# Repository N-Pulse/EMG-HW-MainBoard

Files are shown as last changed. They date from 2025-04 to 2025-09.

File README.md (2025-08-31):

# Electromyography Main Board

This repository contains the PCB design of the EMG bracelet's main board used for EMG signal processing and decoding.
Detailed description of the project can be found in the Documentation folder

This work is licensed under a <a rel="license" href="https://creativecommons.org/licenses/by/4.0/">Creative Commons Attribution 4.0 International License</a>.

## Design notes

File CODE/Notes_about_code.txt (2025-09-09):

NB idk why a .py got inserted in the name, it's really not python

ELEA_Blink : simple blink for ELEA board. All GPIO, UART, SPI etc are already configured (hopefully correctly) in the .ioc file. IMPORTANT : the pre-generated line  PeriphCommonClock_Config() of main.c was commented out because it produced an error that I didn't have time to understand and fix. I think the peripheral clock only concerns some radio stuff, so it should not affect other functions, but who knows ?

ELEA_UART : simple UART communication between STM32 and PC on UART2 using interrupts and callbacks (baud rate 115200). Asks for a key (R,G,B), echoes it back and completes it (R + "ed"). On the Nucleo board this was coded to activate some LEDs, but annoying to set up the pins for that on ELEA. Same remark about PeriphCommonClock_Config() as above.

ELEA_Basic_SPI : it's literally just sending the message "11110001" to the ADC over SPI3. It doesn't mean anything, I just wanted an easily recognizable signal to check on the oscilloscope. Same remark about PeriphCommonClock_Config() as above.

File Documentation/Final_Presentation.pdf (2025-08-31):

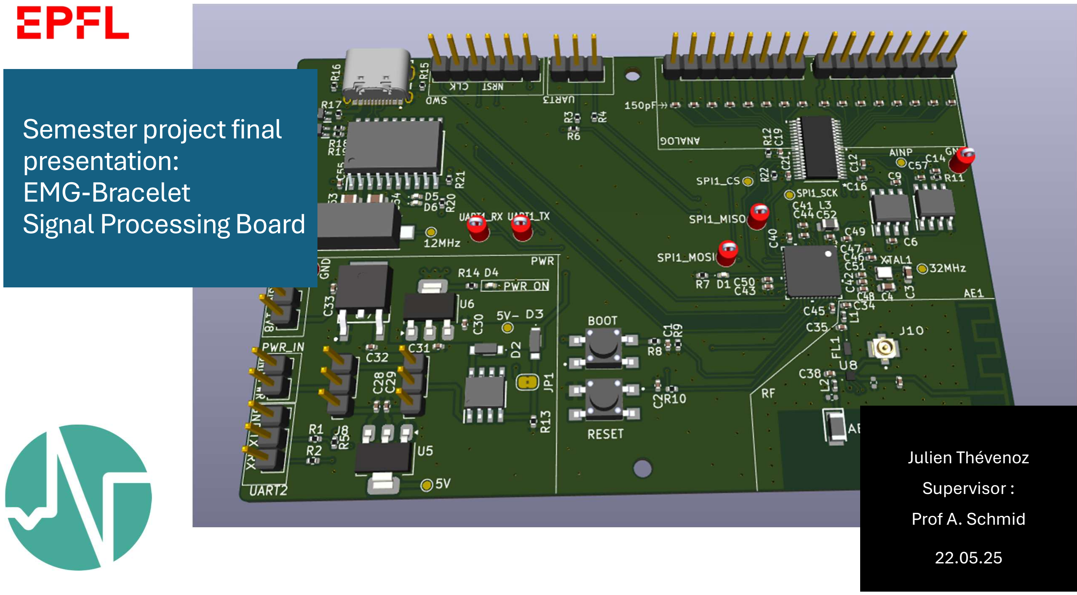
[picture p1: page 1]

## Semester project final presentation: EMG-Bracelet Signal Processing Board

Julien Thévenoz
Supervisor :
Prof A. Schmid

22.05.25

## Table of contents

### 1) Project motivation & goals

### 2) Requirements

### 3) Design choice : Board as prototype

### 4) Product version 1 4.1) Block Diagram 4.2) Schematic 4.3) PCB layout

### 5) Challenges

### 6) Progress

### 7) Demonstrations

### 8) References

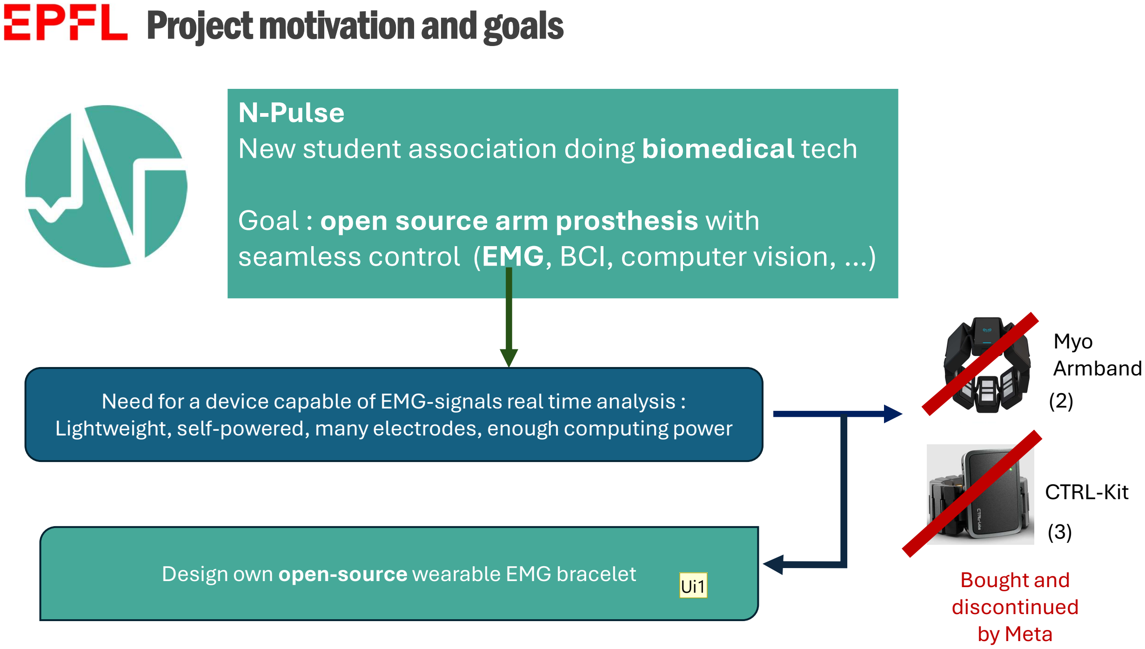
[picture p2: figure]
Project motivation and goals; N-Pulse; Goal : open source arm prosthesis with; CTRL-Kit; Bought and discontinued by Meta; Myo Armband

## New student association doing biomedical tech

## seamless control (EMG, BCI, computer vision, …)

Need for a device capable of EMG-signals real time analysis : Lightweight, self-powered, many electrodes, enough computing power

Design own open-source wearable EMG bracelet

Slide 3

Ui1 | "EMG analysis" implies it only does signal processing, but in our case it also does signal acquisition.=> I would simply say "EMG bracelet". Utilisateur invité, 2025-05-21T22:29:21.107

## Project motivation and goals

«Development of an open-source EMG armband for Hand Gesture Estimation” Semester project by R. Danylovych and E. Massonnet at labs INL & TNE

Based on a design by eLiONS lab (Politecnico Torino) [1] [2] First prototype of EMG signal acquisition modules and bracelet architecture BUT no time to develop module to analyze the signals

Autumn
2024

Spring 2025

ML Semester project proposition : «EMG Signal Processing Board»

•Standalone, wearable, light , ajustable bracelet •Hand gesture detection from EMG signals

•Open-source and documented

Develop the hardware to analyze the EMG signals :

- Able to run compact ML algorithm such as [3] on- board and in real time
- Transmit results wirelessly and physically
- Central piece of the EMG bracelet (powers the rest)

The signal processing board is a component of the N-Pulse EMG Bracelet project :

## Requirements

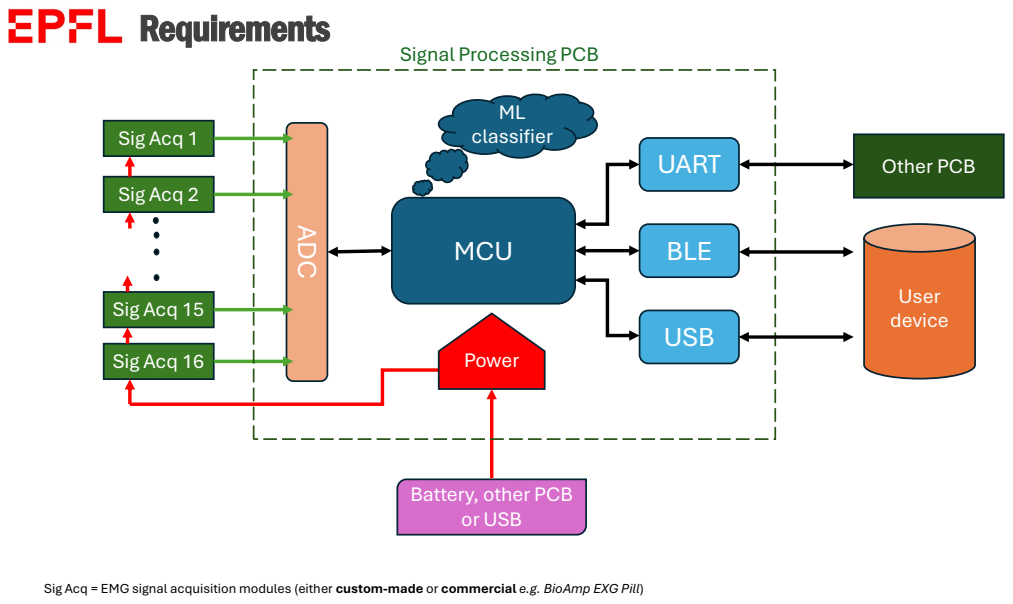
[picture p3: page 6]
MCU ADC; Sig Acq 1; Sig Acq 2; Sig Acq 16; BLE; USB; UART; Sig Acq 15; Power; Other PCB; ML classifier; User device

Signal Processing PCB

Battery, other PCB
or USB

Sig Acq = EMG signal acquisition modules (either custom-made or commercial e.g. BioAmp EXG Pill)

## Requirements

Paper [3] proposes a model with ~7000 parameters to do hand gesture classification This amounts to ~55 kBytes (float double precision 8 Bytes).
Another paper proposes a model with 400’000 parameters [4] ~ 2.6 Mbytes, and then others with even more.
We want to base software on [3] and decided that a flash memory of 2 MB should be enough. For RAM, we calculated that 1s of data ~ 100kBytes.

16 channels @ 800 Hz each --> ADC sampling rate > 12 800 Hz. But accounting for channel switching, non-ideal SigAcq modules etc -> decided 100 Samples per Second strict minimum

Enough FLASH, RAM and clock frequency to run on-board ML algorithm in real-time.
MCU | Bluetooth capability. ADC

## Design choice : board as prototype

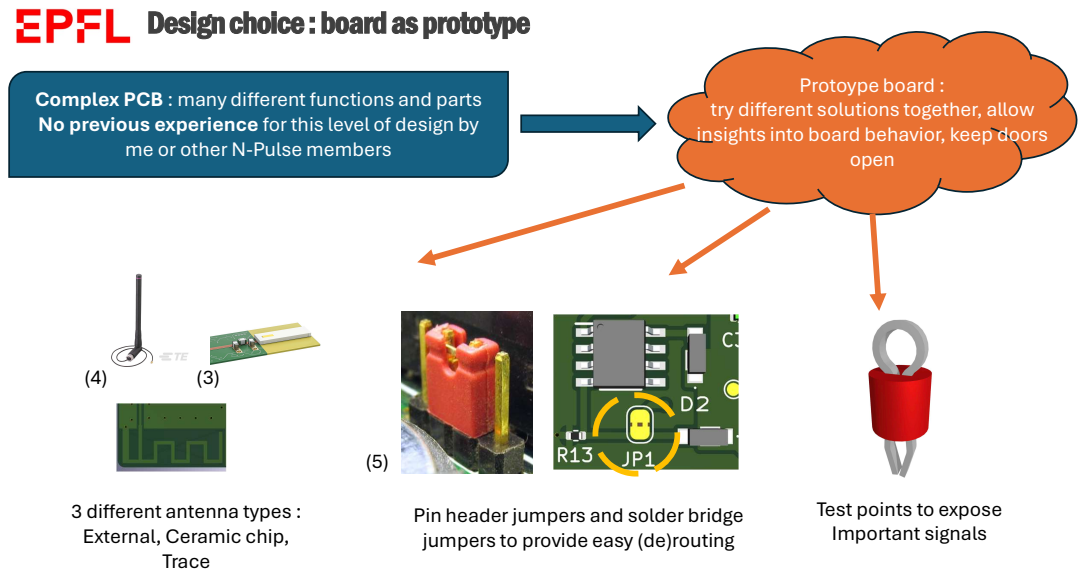
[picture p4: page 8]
Protoype board :; open; Trace

Complex PCB : many different functions and parts
No previous experience for this level of design by

try different solutions together, allow
insights into board behavior, keep doors

me or other N-Pulse members

Test points to expose
Important signals

3 different antenna types :
External, Ceramic chip,

Pin header jumpers and solder bridge
jumpers to provide easy (de)routing

## Signal Processing Board : Version 1

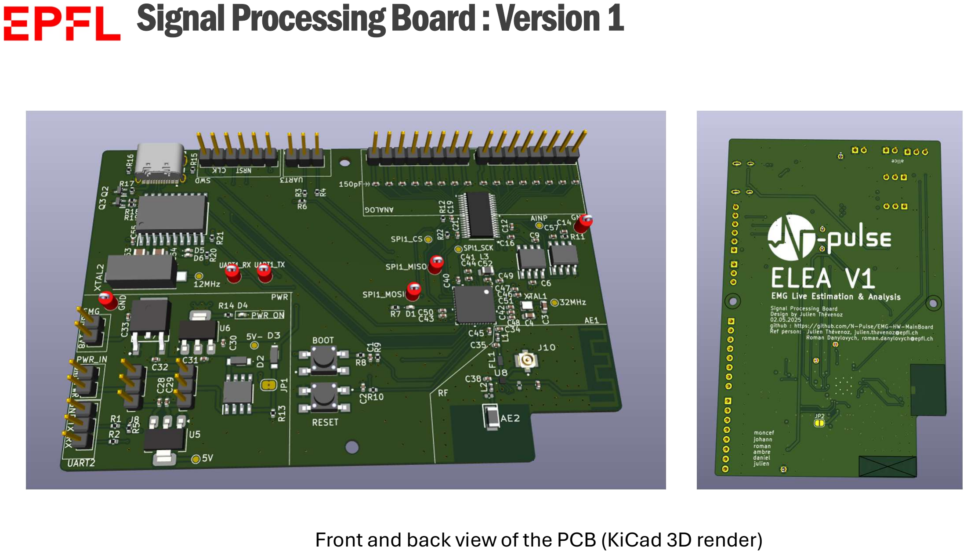
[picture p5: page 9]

Front and back view of the PCB (KiCad 3D render)

## Block diagram

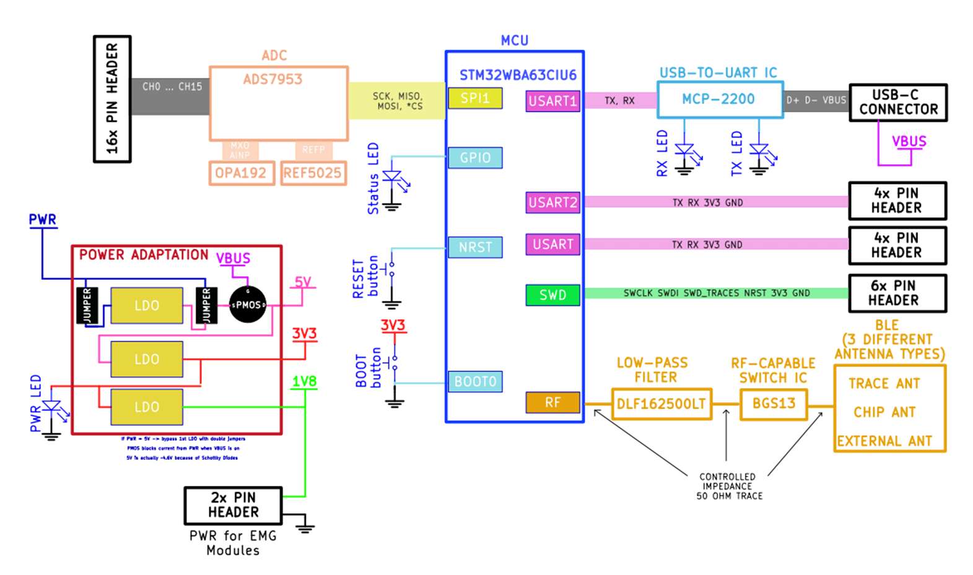
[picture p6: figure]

## Schematic

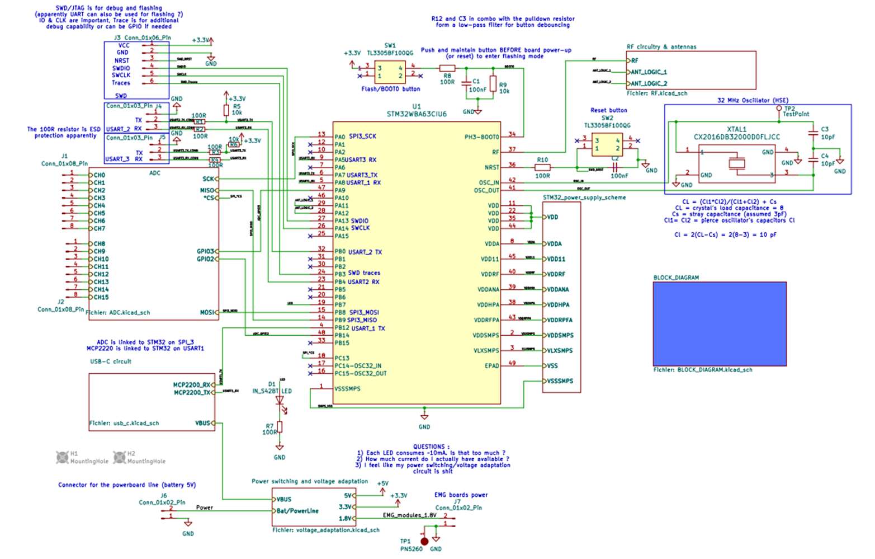
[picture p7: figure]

Electronic schematic main page

## Schematic

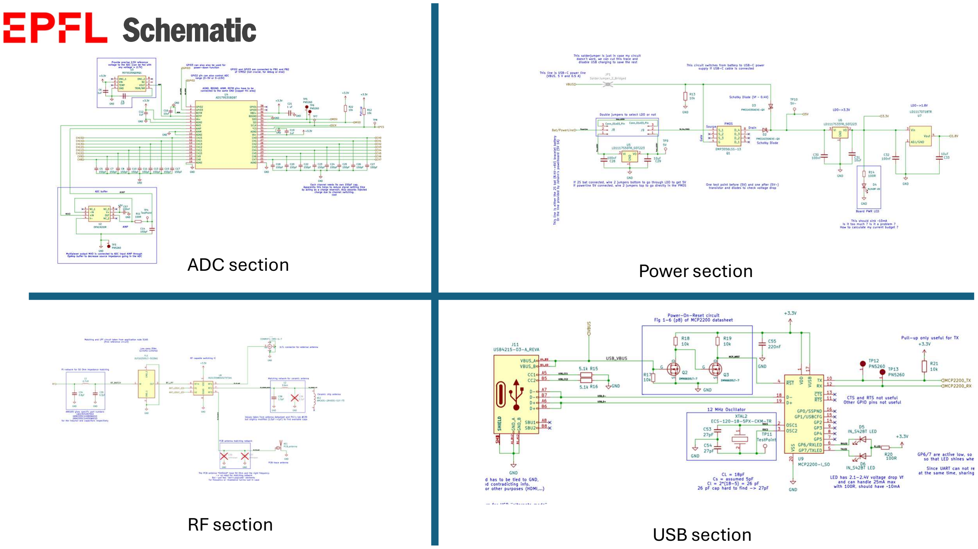
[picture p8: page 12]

RF section

Power section

USB section

ADC section

## PCB LAYOUT – 4 LAYERS

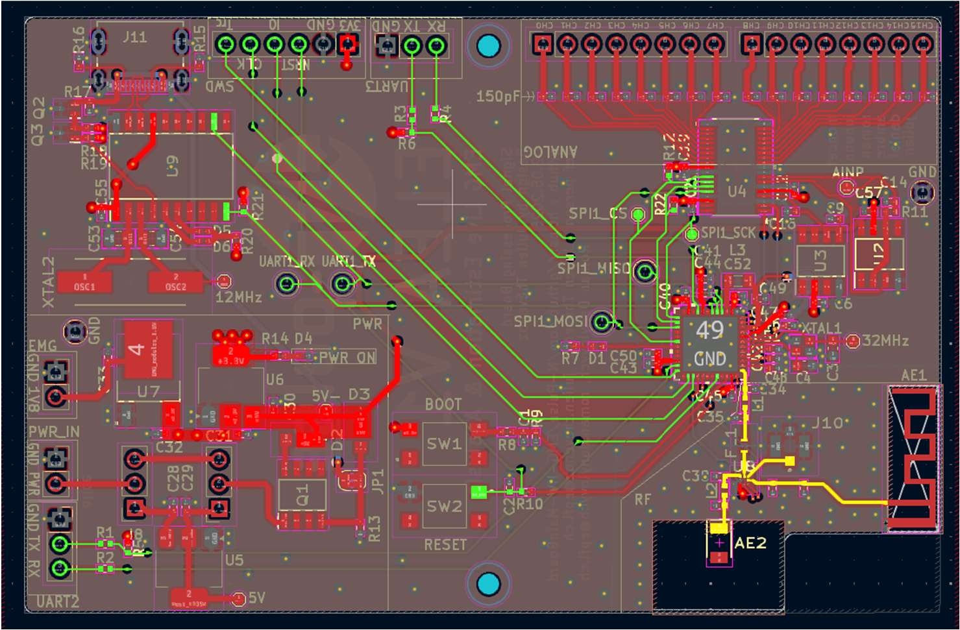
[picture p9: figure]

## PCB LAYOUT

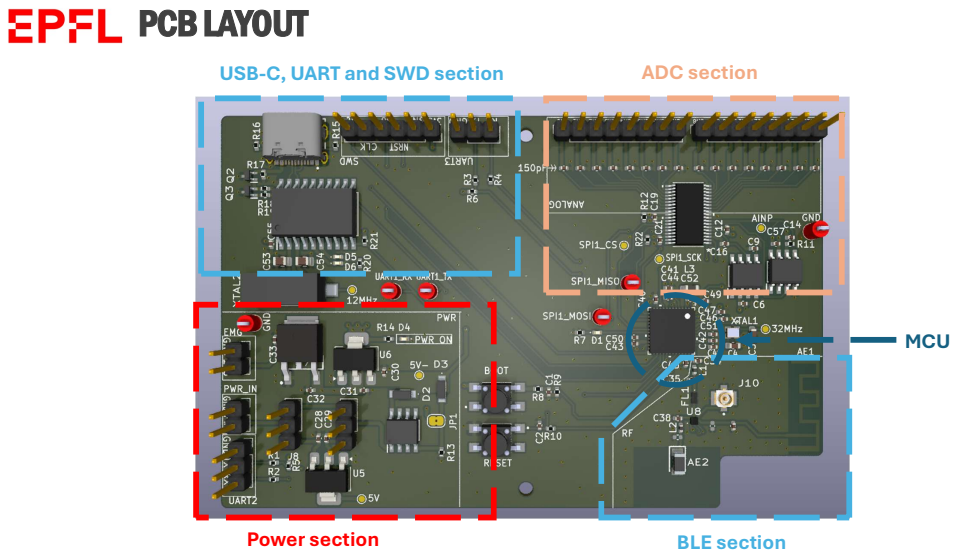
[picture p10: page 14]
Power section; BLE section; USB-C, UART and SWD section; ADC section; MCU

## PCB LAYOUT

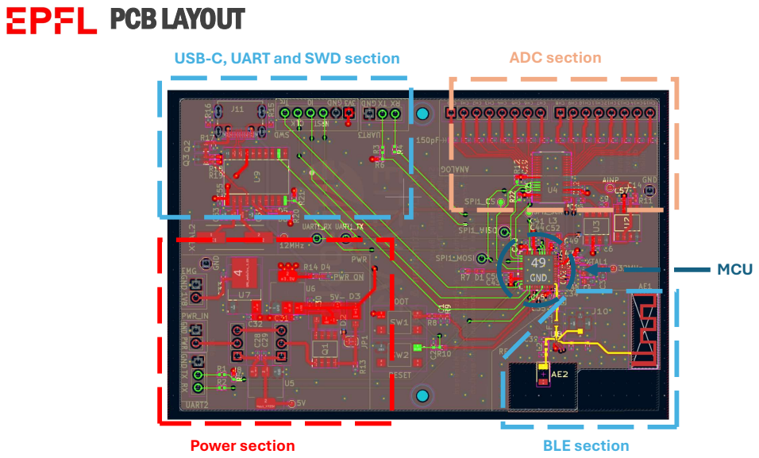
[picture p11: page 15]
Power section; BLE section; USB-C, UART and SWD section; ADC section; MCU

## PCB LAYOUT – 4 LAYERS

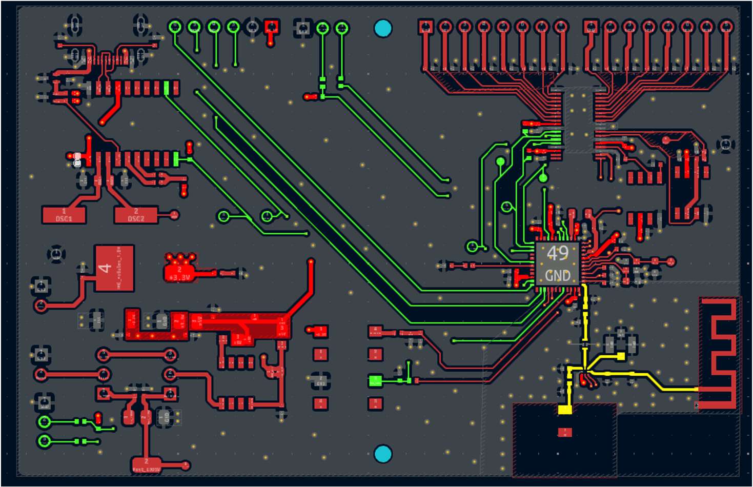
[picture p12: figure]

## PCB LAYOUT – FRONT LAYER (SIGNAL, RF)

## PCB LAYOUT – 2nd LAYER (GND)

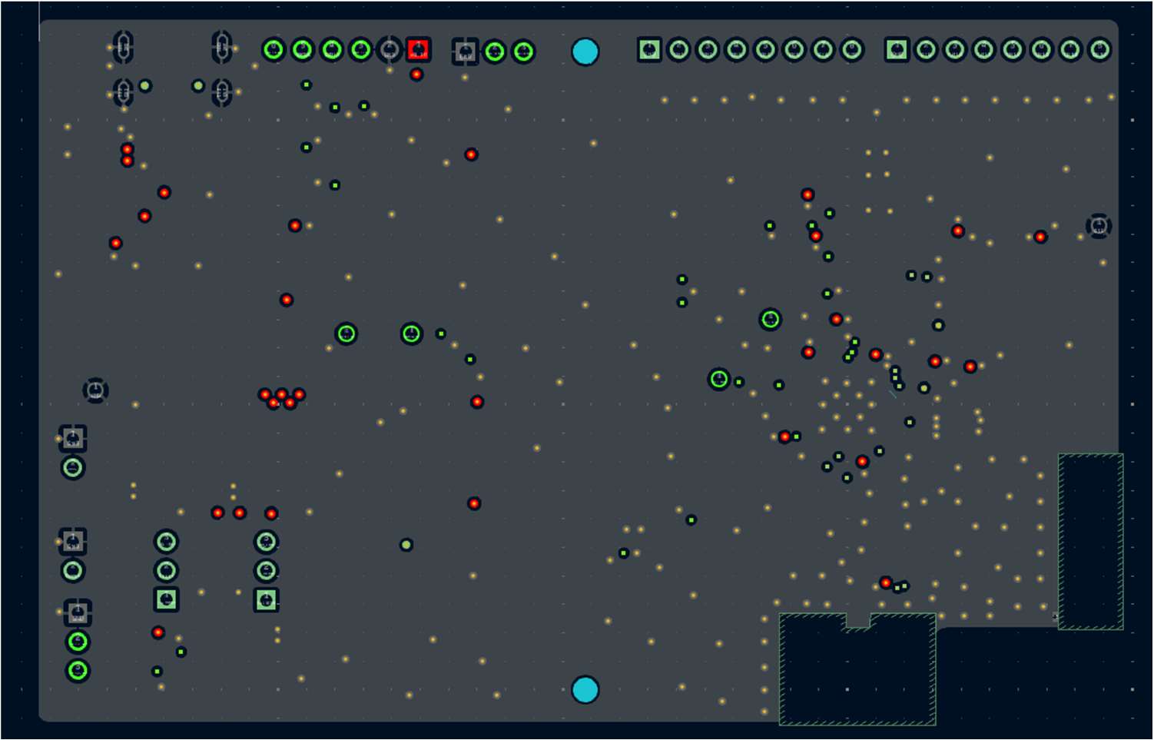
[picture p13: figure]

## PCB LAYOUT – 3rd LAYER (3.3V)

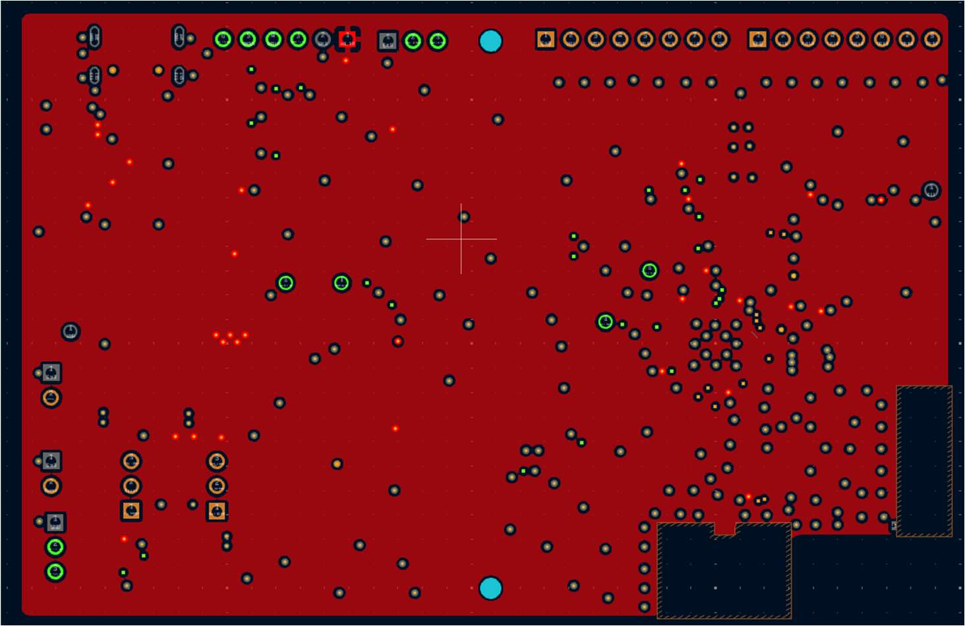
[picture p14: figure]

## PCB LAYOUT – BOTTOM LAYER (SIGNAL)

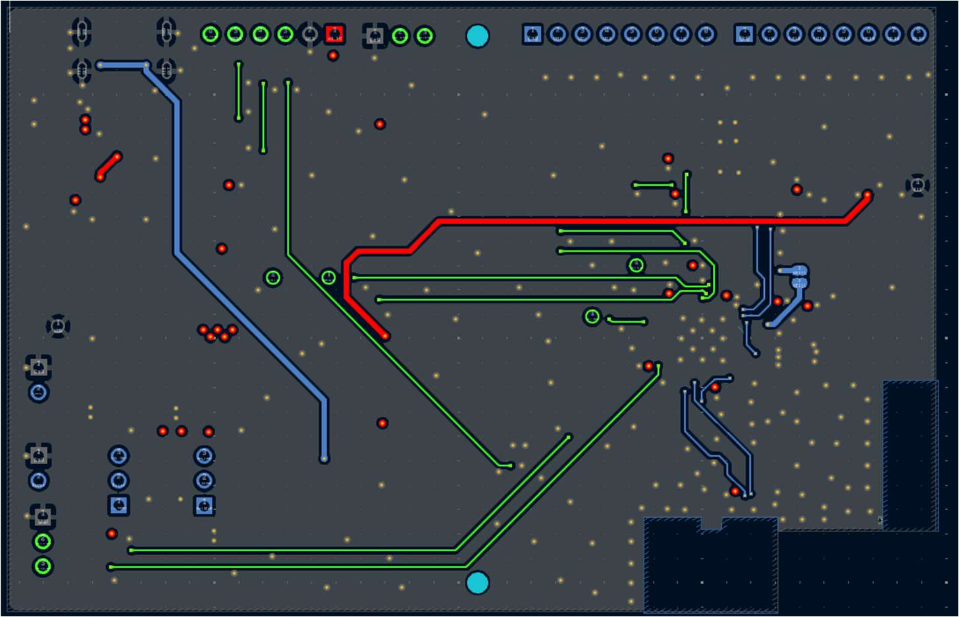
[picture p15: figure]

## Challenges

1) Some goals still slightly vague
2) No prior experience
3) Workload
4) RF

## Self-teaching

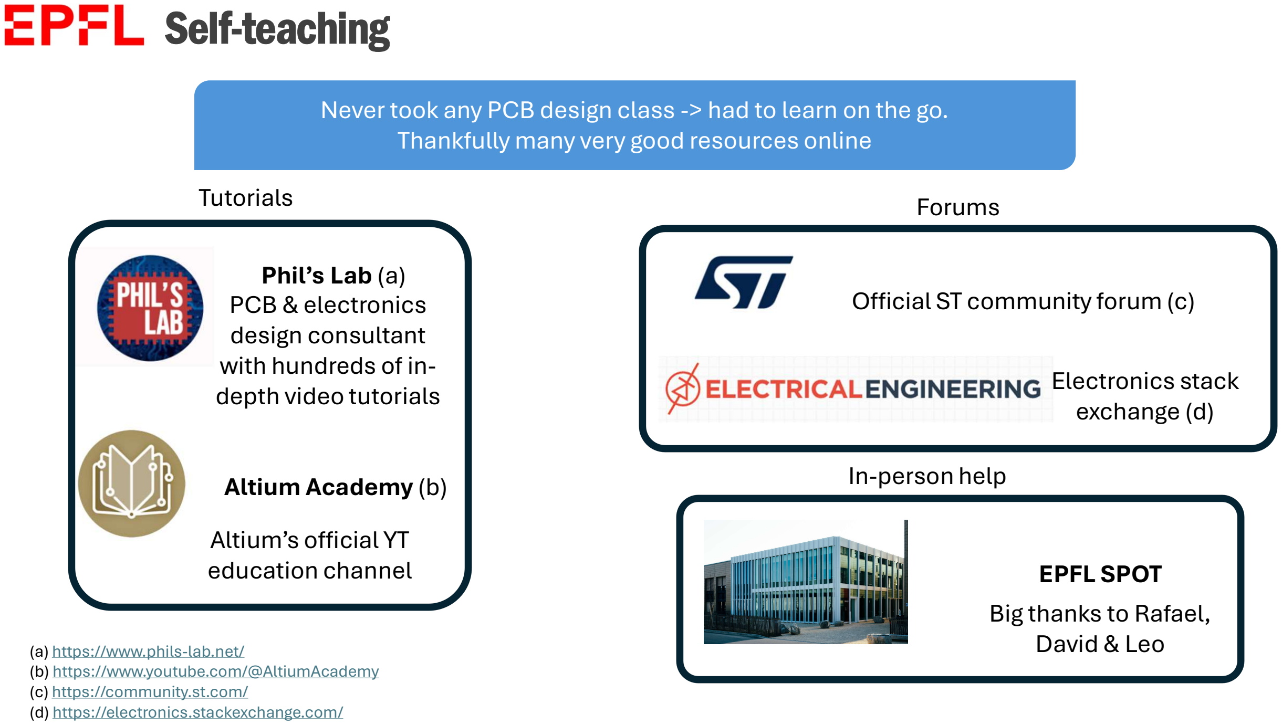
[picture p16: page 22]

(a) https://www.phils-lab.net/
(b) https://www.youtube.com/@AltiumAcademy
(c) https://community.st.com/
(d) https://electronics.stackexchange.com/

Never took any PCB design class -> had to learn on the go. Thankfully many very good resources online

Tutorials

PCB & electronics
design consultant
with hundreds of indepth video tutorials

Altium’s official YT
education channel

Forums

In-person help

Electronics stack
exchange (d)

Phil’s Lab (a)

Altium Academy (b)

EPFL SPOT
Big thanks to Rafael,
David & Leo

Official ST community forum (c)

## Progress so far

- Design
- List of improvement ideas for next iteration
- Extensive list of notes on conception process
- Assemble
- Test individual composants
- Shape improvement ideas and notes into a coherent tutorial N-Pulse members

## Demonstrations : UART communication

Goal : Use UART to command Nucleo Board (STM32) to switch LEDs on/off from PC

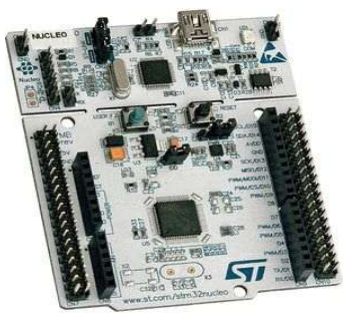
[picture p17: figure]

ST Nucleo F446RE board (6)

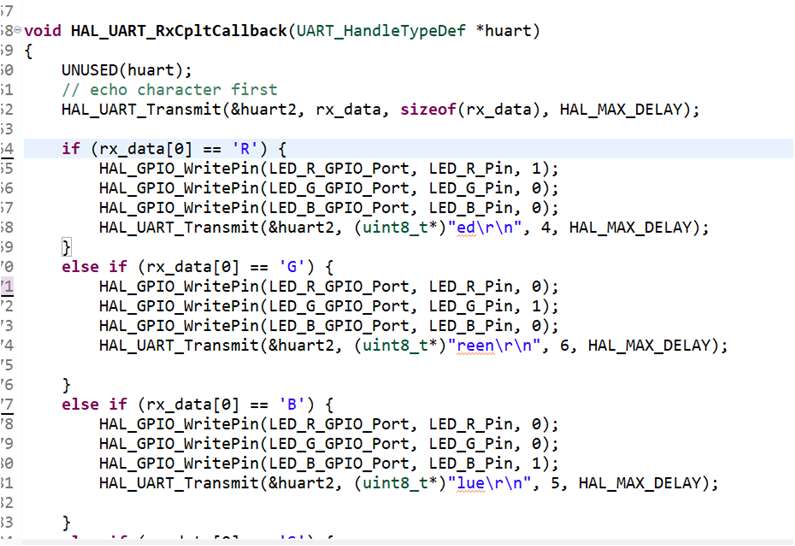
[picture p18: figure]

Code snippet : using interrupt callbacks to command LEDs in non-blocking way
(in STM32CubeIDE)

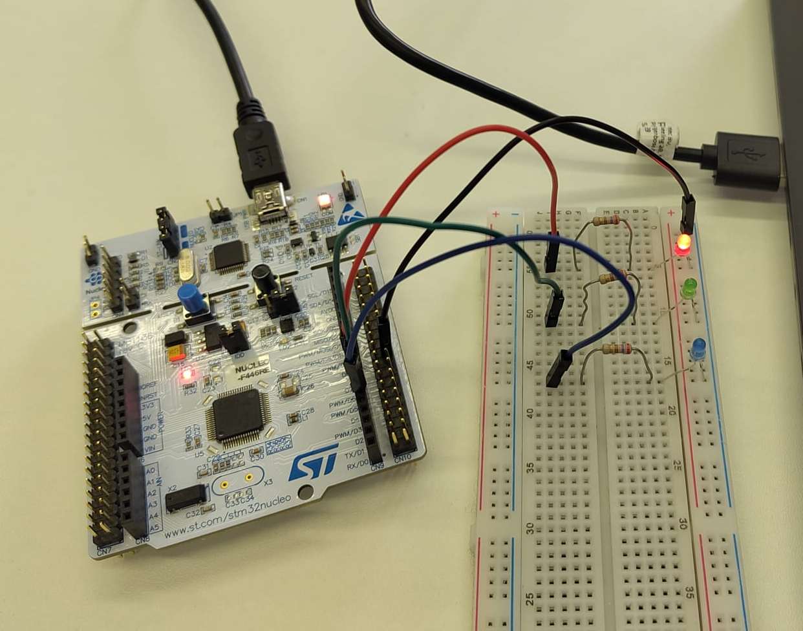
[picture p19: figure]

Setup

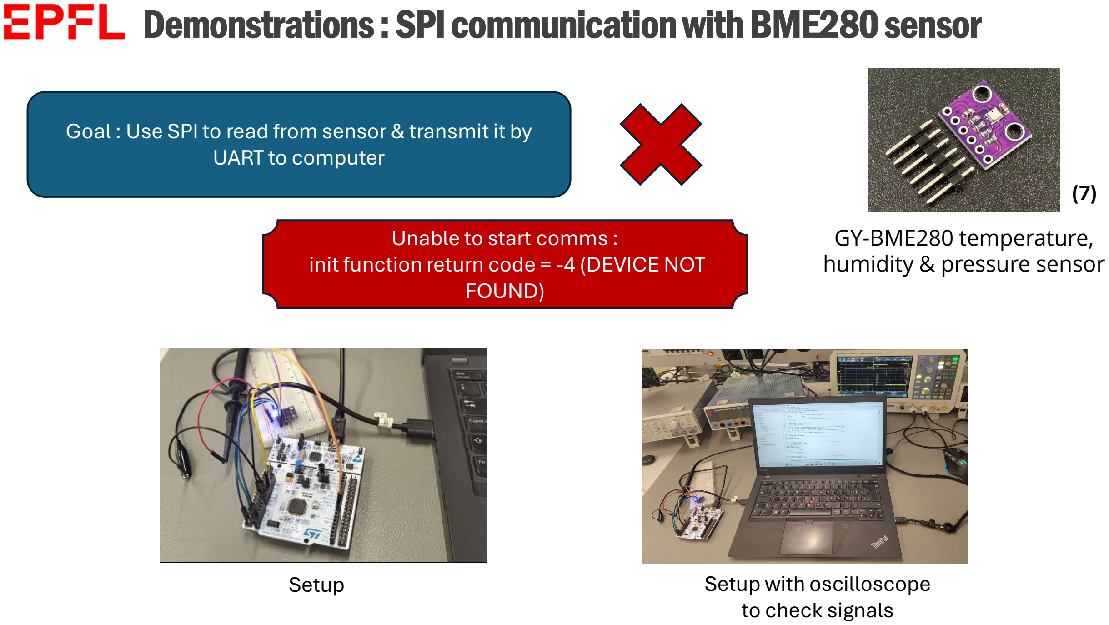
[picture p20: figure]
UART to computer; GY-BME280 temperature, humidity & pressure sensor; Unable to start comms :; FOUND); Setup with oscilloscope to check signals; Setup

## Demonstrations : SPI communication with BME280 sensor

Goal : Use SPI to read from sensor & transmit it by

init function return code = -4 (DEVICE NOT

## Demonstrations : SPI communication with BME280 sensor

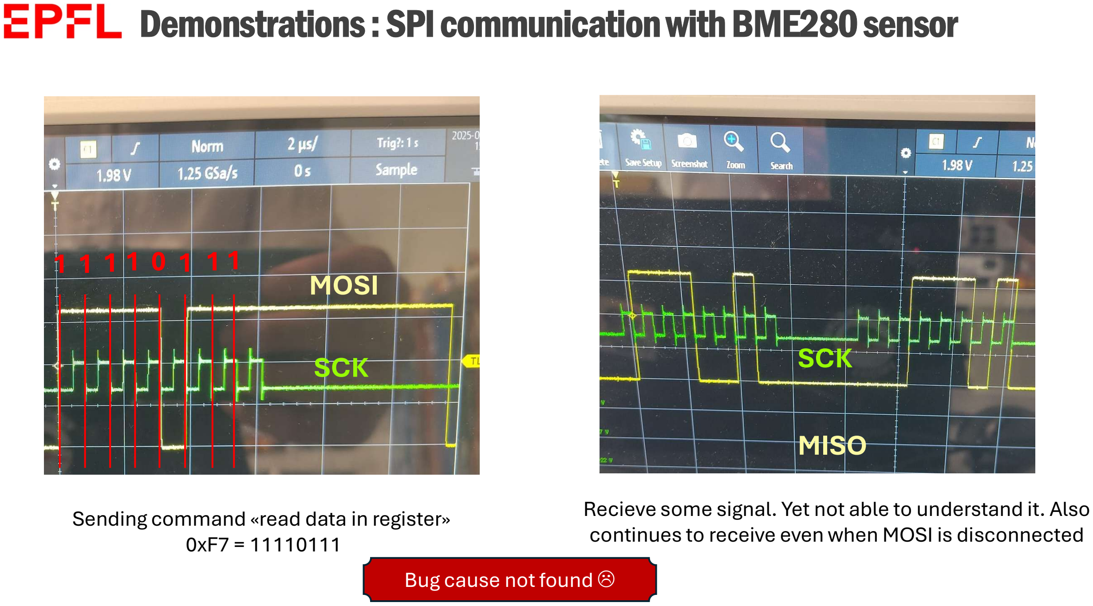
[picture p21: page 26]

1 1 1 1 0 1 1 1

## SCK

## MOSI

Sending command «read data in register» 0xF7 = 11110111

## SCK

## MISO

Recieve some signal. Yet not able to understand it. Also continues to receive even when MOSI is disconnected Bug cause not found

## References

Images
(1) https://wearables.com/products/myo
(2) https://www.curtisbarbre.com/ctrl-kit
(3) https://www.analogictips.com/matching-service-optimizes-gsm-900-wifi-bluetooth-gps-gnss-zigbee-4g-lte-antenna-placement/
(4) https://www.te.com/en/product-L9000097-01.html
(5) https://en.wikipedia.org/wiki/Pin_header#/media/File:Jumper_on_motherboard.jpg
(6) https://media.distrelec.com/Web/WebShopImages/portrait_medium/23/3f/st-nucleo-30009233f.jpg
(7) https://protosupplies.com/product/gy-bme280-pressure-humidity-temperature-sensor-module/
(8) https://cdn.myportfolio.com/645ef5b2f82fdeaf819364ecd9d55d6c/249fac0f-5e46-40cb-a0d7-fa4df5d45ae8_car_4x3.jpg?h=e5b7b4d92b4ce4867a731d0a88e68f27

## References

Papers
[1] A. Mongardi et al., "Hand Gestures Recognition for Human-Machine Interfaces: A Low-Power Bio-Inspired Armband," in IEEE Transactions on Biomedical Circuits and Systems, vol. 16, no. 6, pp. 1348-1365, Dec. 2022, doi: 10.1109/TBCAS.2022.3211424.
[2] F. Rossi, A. Mongardi, P. M. Ros, M. R. Roch, M. Martina and D. Demarchi, "Tutorial: A Versatile Bio-Inspired System for Processing and Transmission of Muhttps://cdn.myportfolio.com/645ef5b2f82fdeaf819364ecd9d55d6c/249fac0f-5e46-40cb-a0d7-fa4df5d45ae8_car_4x3.jpg?h=e5b7b4d92b4ce4867a731d0a88e68f27scular Information," in IEEE Sensors Journal, vol. 21, no. 20, pp. 22285-22303, 15 Oct.15, 2021, doi: 10.1109/JSEN.2021.3103608.
[3] Kalbasi, Mohammad & Shaeri, Mohammad & Mendez, Vincent & Shokur, Solaiman & Micera, Silvestro & Shoaran, Mahsa. (2024). A Hardware-Efficient EMG Decoder with an Attractor-based Neural Network for Next-Generation Hand Prostheses. 10.48550/arXiv.2405.20052.
[4] A. Ameri, M. A. Akhaee, E. Scheme, and K. Englehart, ”Regression convolutional neural network for improved simultaneous EMG control,”
Journal of Neural Engineering, vol. 16, no. 3, 2019, Art. no. 036015.

## Questions

## Thank you for listening

## Questions ?

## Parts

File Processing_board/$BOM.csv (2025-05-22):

Reference | Qty | Value | DNP | Exclude from Board | MANUFACTURER | Manufacturer_Part_Number | Link
AE1 | 1 | PCB_antenna |  | Exclure du PCB
AE2 | 1 | AMCA31-2R450G-S1F-T3 |  |  | ABRACON | AMCA31-2R450G-S1F-T3 | https://www.mouser.ch/ProductDetail/ABRACON/AMCA31-2R450G-S1F-T3?qs=AAveGqk956GLuOddQEK40Q%3D%3D
C1,C2,C28,C30,C32,C40,C41,C42,C43,C45,C46,C47,C51,C57 | 14 | 100nF |  |  | Samsung Electro-Mechanics | CL05B104KP5VPNC | https://eu.mouser.com/ProductDetail/Samsung-Electro-Mechanics/CL05B104KP5VPNC?qs=gqBM4hNBiUXTv%252BkFO9q2pQ%3D%3D
C3,C4 | 2 | 10pF |  |  | KYOCERA AVX | 0603ZC100KAT2A | https://www.mouser.ch/ProductDetail/KYOCERA-AVX/0603ZC100KAT2A?qs=jGANiKWBgcibzoGXAkKY5Q%3D%3D
C5,C7,C8,C10,C11,C13,C14,C15,C17,C18,C20,C22,C23,C24,C25,C26,C27 | 17 | 150pF |  |  | KEMET | C0402C151K5RACTU | https://www.mouser.ch/ProductDetail/KEMET/C0402C151K5RACTU?qs=bH0hdZQCdBIE%252BjkzdJGatg%3D%3D
C6,C9,C12,C19,C44 | 5 | 1uF |  |  | Samsung Electro-Mechanics | CL05A105KP5NNNC | https://www.mouser.ch/ProductDetail/Samsung-Electro-Mechanics/CL05A105KP5NNNC?qs=X6jEic%2FHinBsUeNeR9HD7w%3D%3D
C16,C29,C31,C33,C50,C52 | 6 | 10uF |  |  | Murata Electronics | GRM155R61A106ME11D | https://www.mouser.ch/ProductDetail/Murata-Electronics/GRM155R61A106ME11D?qs=xZ%2FP%252Ba9zWqZMJSi57Q8OyA%3D%3D
C21 | 1 | 1 uF |  |  | Samsung Electro-Mechanics | CL05A105KP5NNNC | https://www.mouser.ch/ProductDetail/Samsung-Electro-Mechanics/CL05A105KP5NNNC?qs=X6jEic%2FHinBsUeNeR9HD7w%3D%3D
C34 | 1 | 0.8pF |  |  | Murata Electronics | GRM1555C1HR80BA01D | https://www.mouser.ch/ProductDetail/Murata-Electronics/GRM1555C1HR80BA01D?qs=e%252BE4OD6MgMezPYPintwvrA%3D%3D
C35 | 1 | 0.3pF |  |  | Murata Electronics | GRM1555C1HR30WA01D | https://www.mouser.ch/ProductDetail/Murata-Electronics/GRM1555C1HR30WA01D?qs=e%252BE4OD6MgMcS%252BbE0ktTutg%3D%3D
C38 | 1 | 1.5pF |  |  | Walsin | 0402N1R5B100CT | https://www.mouser.ch/ProductDetail/Walsin/0402N1R5B100CT?qs=ZrPdAQfJ6DObCBhS8paADQ%3D%3D
C48 | 1 | 470nF |  |  | KEMET | C0402C473K8RACAUTO7411 | https://www.mouser.ch/ProductDetail/KEMET/C0402C473K8RACAUTO7411?qs=sSYV1F9c5cEF%2FA7Et64KMA%3D%3D
C49 | 1 | 4.7uF |  |  | YAGEO | CC0402KRX5R6BB475 | https://www.mouser.ch/ProductDetail/YAGEO/CC0402KRX5R6BB475?qs=tS%2FAHvPQ%2F57yk%252BaeAkyovA%3D%3D
C53,C54 | 2 | 27pF |  |  | KYOCERA AVX | 08055C270KAT2A | https://www.mouser.ch/ProductDetail/KYOCERA-AVX/08055C270KAT2A?qs=ykEKLGTiBcy%2FccVg1dGO5g%3D%3D
C55 | 1 | 220nF |  |  | Murata Electronics | GRT155R71A224KE01D | https://www.mouser.ch/ProductDetail/Murata-Electronics/GRT155R71A224KE01D?qs=qkDYIeTQ%252BEkMujM%252BGJvzUg%3D%3D
D1,D4,D5,D6 | 4 | IN_S42BT LED |  |  | Inolux | IN-S42BT5G | https://www.mouser.ch/ProductDetail/Inolux/IN-S42BT5G?qs=mAH9sUMRCttW6d2tLN392Q%3D%3D
D2,D3 | 2 | PMEG4030AEXE-QX |  |  | Nexperia | PMEG4030AEXE-QX | https://www.mouser.ch/ProductDetail/Nexperia/PMEG4030AEXE-QX?qs=olJun0bQHM9XKv%2FbcqOajw%3D%3D
FL1 | 1 | DLF162500LT-5028A1 |  |  | TDK | DLF162500LT-5028A1 | https://www.mouser.ch/ProductDetail/TDK/DLF162500LT-5028A1?qs=U%2FZX79kHR%2FlwIbAISCs3qA%3D%3D
H1,H2 | 2 | MountingHole |  | Exclure du PCB
J1,J2 | 2 | Conn_01x08_Pin
J3 | 1 | Conn_01x06_Pin
J4,J5,J8,J9 | 4 | Conn_01x03_Pin
J6,J7 | 2 | Conn_01x02_Pin
J10 | 1 | CONMHF1-SMD-G-T |  |  | TE Connectivity / Linx Technologies | CONMHF1-SMD-G-T | https://www.mouser.ch/ProductDetail/TE-Connectivity-Linx-Technologies/CONMHF1-SMD-G-T?qs=7D1LtPJG0i0JqNJVGTgWfg%3D%3D
J11 | 1 | USB4215-03-A_REVA |  |  | CGT | USB4215-03-A | https://www.mouser.ch/ProductDetail/GCT/USB4215-03-A?qs=IKkN%2F947nfBipec8wvDabA%3D%3D
JP1 | 1 | SolderJumper_2_Bridged
JP2 | 1 | SolderJumper_2_Open
L1 | 1 | 2.7nH |  |  | Murata Electronics | LQG15HS2N7S02D | https://www.mouser.ch/ProductDetail/Murata-Electronics/LQG15HS2N7S02D?qs=ctz47l0uL1AKrLI74yO5Qw%3D%3D
L2 | 1 | 3.9nH |  |  | TE Connectivity / Sigma Inductors | 36550402S3N9T | https://www.mouser.ch/ProductDetail/TE-Connectivity-Sigma-Inductors/36550402S3N9T?qs=i8QVZAFTkqQazOkGct7ESA%3D%3D
L3 | 1 | 2.2uH |  |  | Wurth Elektronik | 74479774222 | https://www.mouser.ch/ProductDetail/Wurth-Elektronik/74479774222?qs=%252BUQ4csG8Rsd58%2FKCVoLnRw%3D%3D
Q1 | 1 | DMP3056LSS-13 |  |  | Diodes Incorporated | DMP3056LSS-13 | https://www.mouser.ch/ProductDetail/Diodes-Incorporated/DMP3056LSS-13?qs=oUsD4qhOtFyEnPLZKitYRA%3D%3D
Q2,Q3 | 2 | DMN66D0LT-7 |  |  | Diodes Incorporated | DMN66D0LT-7 | https://www.mouser.ch/ProductDetail/Diodes-Incorporated/DMN66D0LT-7?qs=ptj1V1atRApcnSIo%2FSL0QQ%3D%3D
R1,R2,R3,R4,R7,R8,R10,R11,R14,R20 | 10 | 100R |  |  | KOA Speer | RK73B1ETTPD101J | https://www.mouser.ch/ProductDetail/KOA-Speer/RK73B1ETTPD101J?qs=7ZBenkSduJQ3N2lLjwh2jA%3D%3D
R5,R6,R9,R12,R13,R17,R18,R19,R21,R22 | 10 | 10k |  |  | Wurth Elektronik | 560112110020 | https://www.mouser.ch/ProductDetail/Wurth-Elektronik/560112110020?qs=mELouGlnn3fA8%252B%2F79%2FueqA%3D%3D
R15,R16 | 2 | 5.1k |  |  | YAGEO | AC0402JR-075K1L | https://www.mouser.ch/ProductDetail/YAGEO/AC0402JR-075K1L?qs=ygRr%2Ftkhtev1AbJgasJMAQ%3D%3D
SW1,SW2 | 2 | TL3305BF100QG |  |  | E-Switch | TL3305BF100QG | https://www.mouser.ch/ProductDetail/E-Switch/TL3305BF100QG?qs=IKkN%2F947nfDIPwqPQja%252BvQ%3D%3D
TP1,TP3,TP5,TP6,TP12,TP13 | 6 | PN5260 |  |  | Keystone | 5260 | https://www.mouser.ch/ProductDetail/Keystone-Electronics/5260?qs=W%2FMpXkg%252BdQ5ZyD03UfNp6A%3D%3D
TP2,TP4,TP7,TP8,TP11 | 5 | TestPoint |  | Exclure du PCB
TP9 | 1 | 5V |  | Exclure du PCB
TP10 | 1 | 5V- |  | Exclure du PCB
U1 | 1 | STM32WBA63CIU6 |  |  | STMicroelectronics | STM32WBA63CIU6 | https://www.mouser.ch/ProductDetail/STMicroelectronics/STM32WBA63CIU6?qs=a2MtRaTmNORvrgIwkIejkg%3D%3D
U2 | 1 | OPA192IDR |  |  | TI | OPA192IDR | https://www.mouser.ch/ProductDetail/Texas-Instruments/OPA192IDR?qs=wrT8kFYR77%252BLV20WgpFlnQ%3D%3D
U3 | 1 | REF5025AQDRQ1 |  |  | TI | REF5025AQDRQ1 | https://www.mouser.ch/ProductDetail/Texas-Instruments/REF5025AQDRQ1?qs=jnnG3uwte7w8iuVSV8mElA%3D%3D
U4 | 1 | ADS7953SBDBT |  |  | TI | ADS7953SBDBT | https://www.mouser.ch/ProductDetail/Texas-Instruments/ADS7953SBDBT?qs=Lv5%252BaqTFJEPgQ17SA2TUyg%3D%3D
U5 | 1 | LD1117S50TR_SOT223 |  |  | STMicroelectronics | LD1117S50TR | https://www.mouser.ch/ProductDetail/STMicroelectronics/LD1117S50TR?qs=eQN2Ig5lfEwsh0kTXN%2FkTg%3D%3D
U6 | 1 | LD1117S33TR_SOT223 |  |  | STMicroelectronics | LD1117S33TR | https://www.mouser.ch/ProductDetail/STMicroelectronics/LD1117S33TR?qs=edoyzKMbmhntQZx4BFmoqw%3D%3D
U7 | 1 | LD1117DT18TR |  |  | STMicroelectronics | LD1117DT18TR | https://www.mouser.ch/ProductDetail/STMicroelectronics/LD1117DT18TR?qs=rkyzKKi%2FrgiTGfkwrcFd%252BA%3D%3D
U8 | 1 | BGS13SN8E6327XTSA1 |  |  | Infineon Technologies | BGS13SN8E6327XTSA1 | https://www.mouser.ch/ProductDetail/Infineon-Technologies/BGS13SN8E6327XTSA1?qs=0DP5yvOrqYmFtfP%252BZ8kQgQ%3D%3D
U9 | 1 | MCP2200-I_SO |  |  | Microchip Technology | MCP2200-I/SO | https://www.mouser.ch/ProductDetail/Microchip-Technology/MCP2200-I-SO?qs=kI7nsUnms46fN8L9VZlJCA%3D%3D
XTAL1 | 1 | CX2016DB32000D0FLJCC |  |  | KYOCERA AVX | CX2016DB32000D0FLJCC | https://www.mouser.ch/ProductDetail/KYOCERA-AVX/CX2016DB32000D0FLJCC?qs=k8ubvZJoN9AkB0G5%2Fsjh3g%3D%3D
XTAL2 | 1 | ECS-120-18-5PX-CKM-TR |  |  | ECS | ECS-120-18-5PX-CKM-TR | https://www.mouser.ch/ProductDetail/ECS/ECS-120-18-5PX-CKM-TR?qs=7MVldsJ5UaxGiQ3V9H8iDw%3D%3D
C36,C37 | 2 | Unknown | DNP | Exclure du PCB
C39 | 1 | 1.5pF | DNP | Exclure du PCB

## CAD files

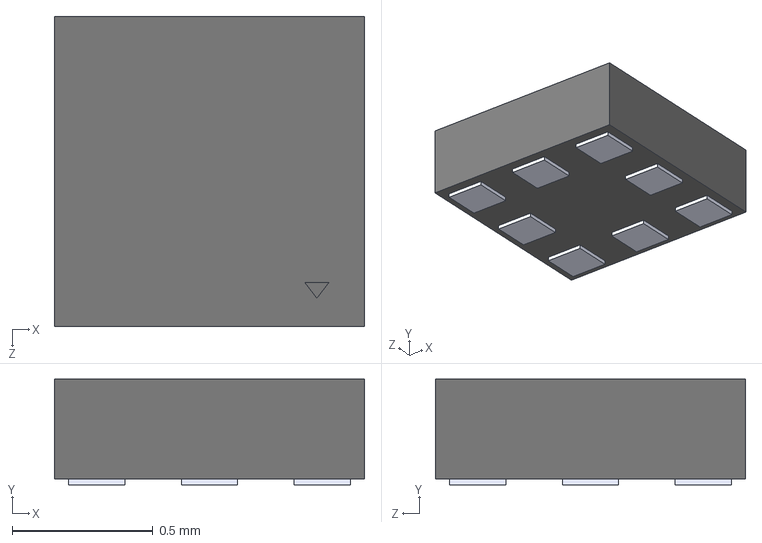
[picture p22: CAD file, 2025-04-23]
Processing_board/CAD models/BGS13SN8E6327XTSA1/BGS13SN8E6327XTSA1.stp
1.10 x 0.375 x 1.10 mm

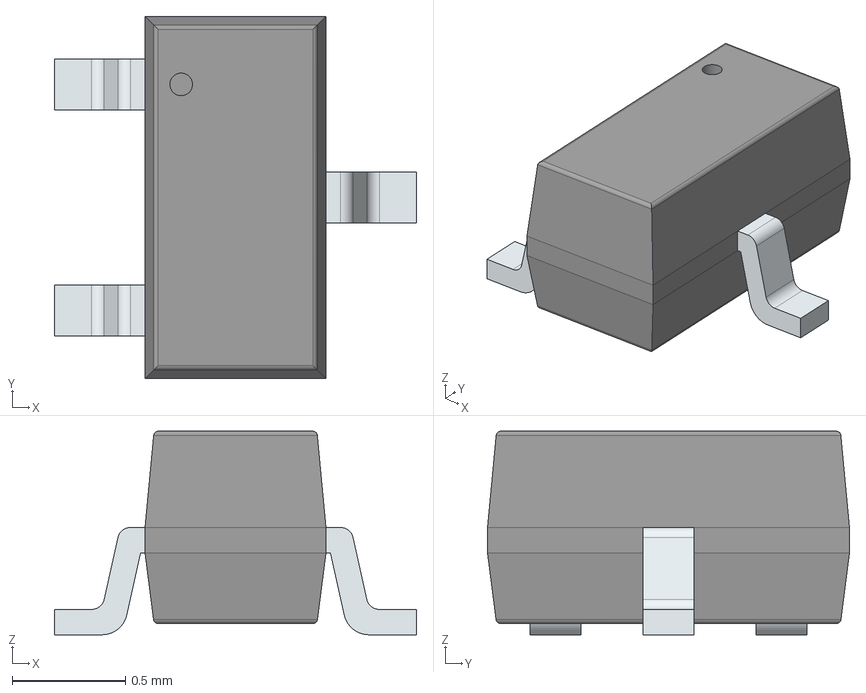
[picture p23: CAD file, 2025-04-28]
Processing_board/CAD models/DMN66D0LT-7/DMN66D0LT-7.stp
1.60 x 1.60 x 0.9 mm
PinsArrayL
FilletPinR

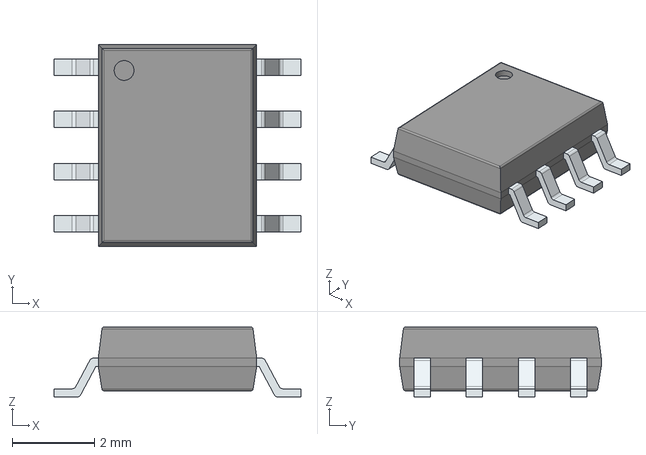
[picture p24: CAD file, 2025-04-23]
Processing_board/CAD models/DMP3056LSS-13/DMP3056LSS-13.stp
6.00 x 4.90 x 1.70 mm
PinsArrayLR

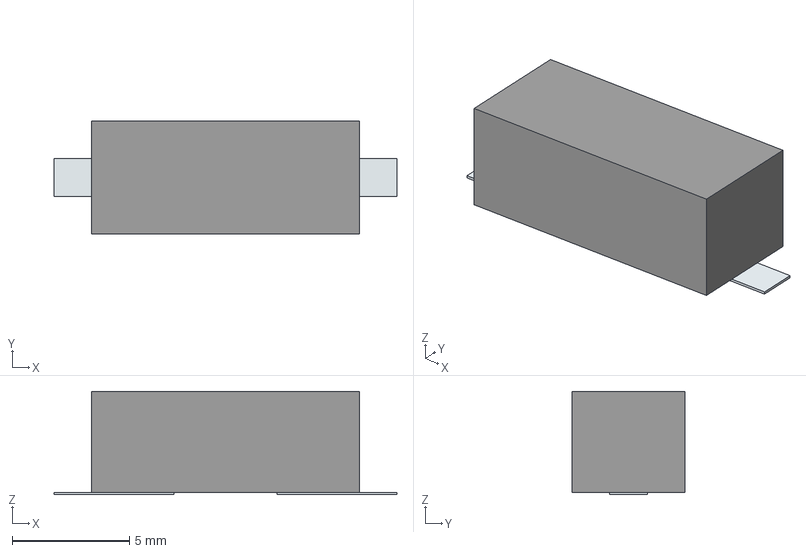
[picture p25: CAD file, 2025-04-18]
Processing_board/CAD models/ECS-120-18-5PX-CKM-TR/ECS-120-18-5PX-CKM-TR.stp
14.6 x 4.80 x 4.40 mm
Pins

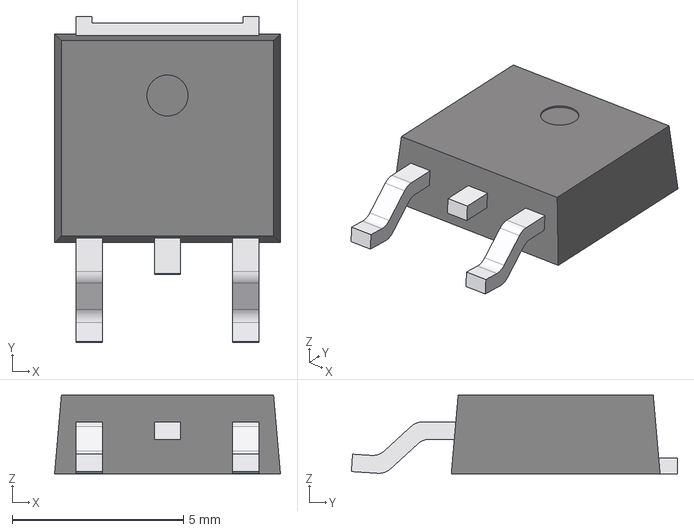
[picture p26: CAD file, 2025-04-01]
Processing_board/CAD models/LD1117DT18TR/LD1117DT18TR.stp
6.60 x 9.53 x 2.30 mm

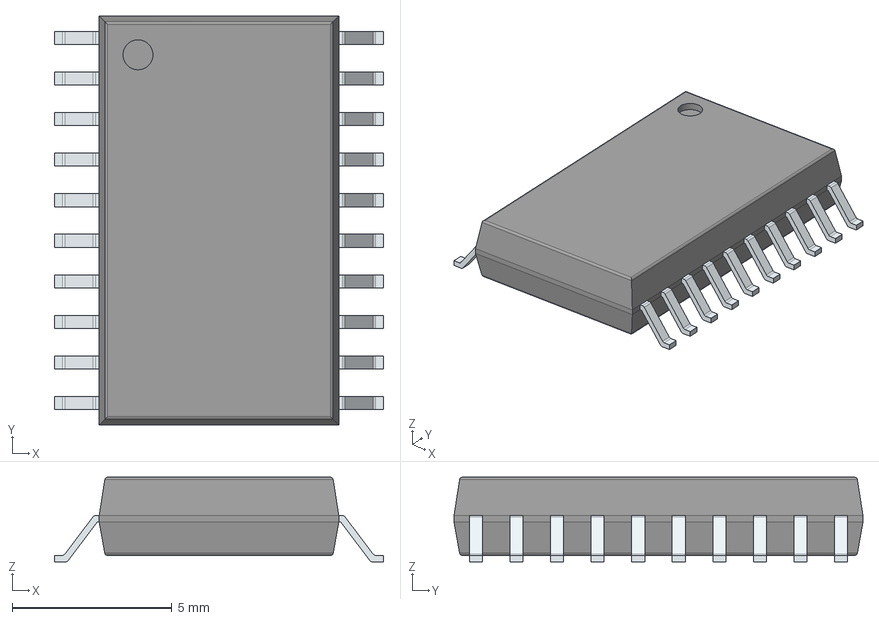
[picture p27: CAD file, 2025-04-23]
Processing_board/CAD models/MCP2200-I_SO/MCP2200-I_SO.stp
10.3 x 12.8 x 2.65 mm
PinsArrayLR

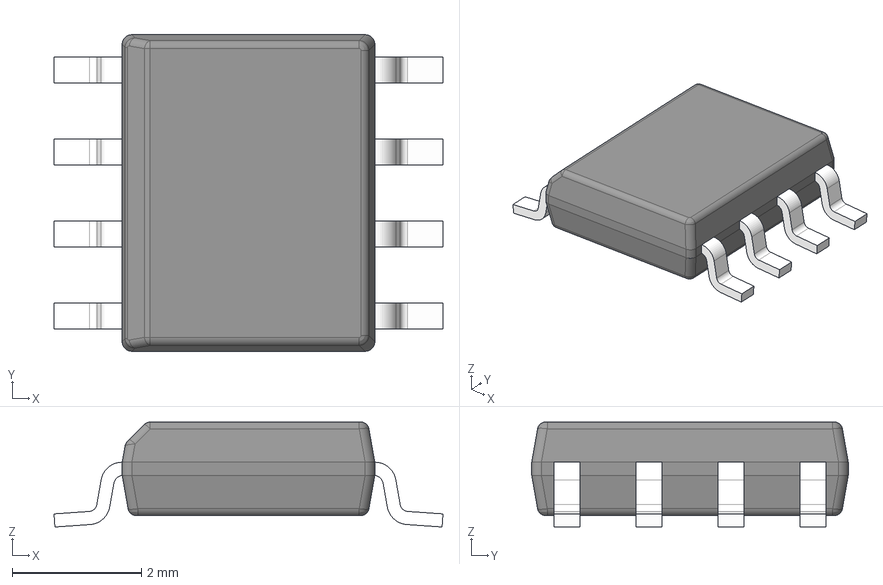
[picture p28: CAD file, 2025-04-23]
Processing_board/CAD models/OPA192IDR/OPA192IDR.stp
6.02 x 4.90 x 1.63 mm
BODY-SO
LEAD-D0008A x 8

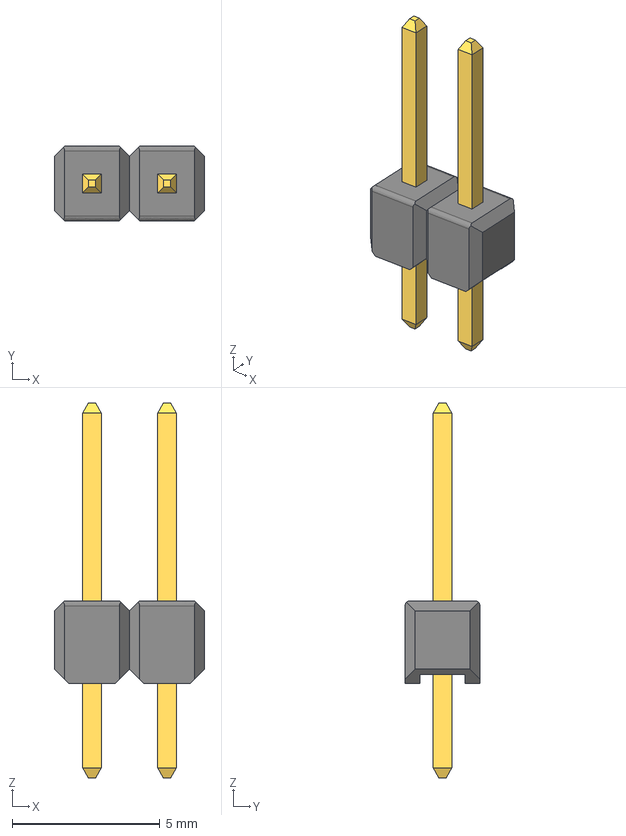
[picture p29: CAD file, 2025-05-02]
Processing_board/CAD models/PinHeaders/Pin Header 1x2 TH Pitch 2.54mm.stp
5.08 x 2.54 x 12.7 mm

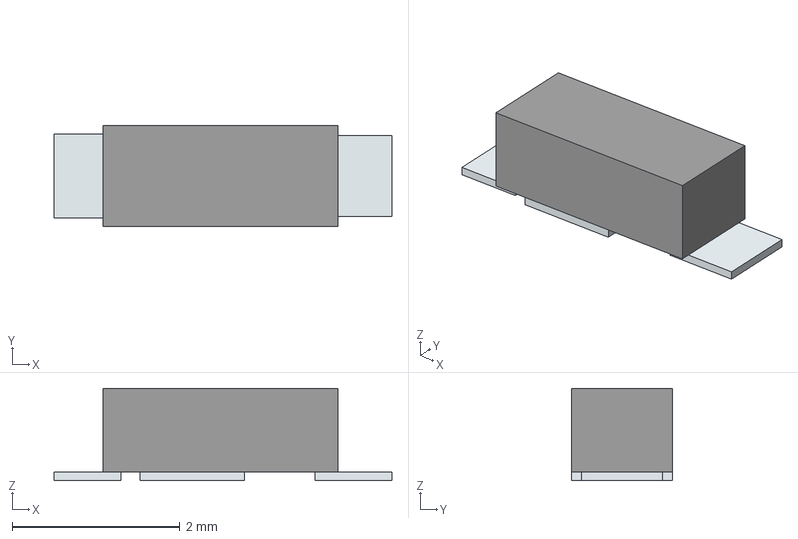
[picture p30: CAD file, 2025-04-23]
Processing_board/CAD models/PMEG4030AEXE-QX/PMEG4030AEXE-QX.stp
4.03 x 1.20 x 1.10 mm
Pins

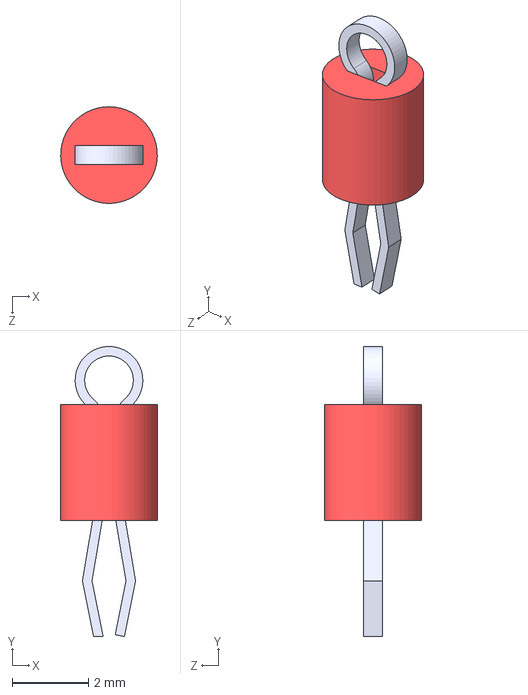
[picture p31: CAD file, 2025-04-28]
Processing_board/CAD models/PN5260/PN5260.STEP
2.54 x 7.62 x 2.54 mm

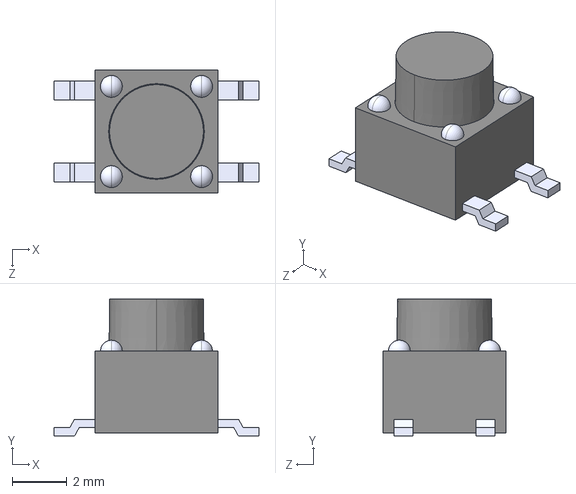
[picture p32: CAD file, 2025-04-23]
Processing_board/CAD models/TL3305BF100QG/TL3305BF100QG.stp
7.50 x 5.00 x 4.50 mm

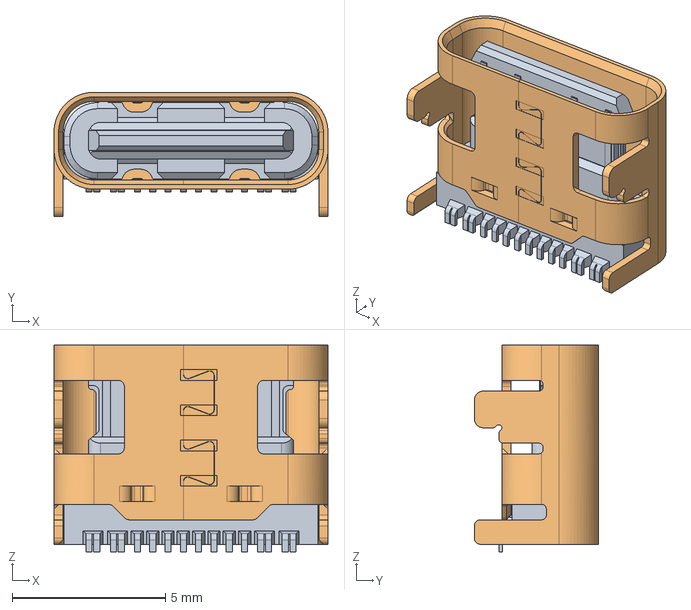
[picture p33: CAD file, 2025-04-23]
Processing_board/CAD models/USB4215_03_A/usb4215-03-a.stp
8.94 x 4.06 x 6.75 mm

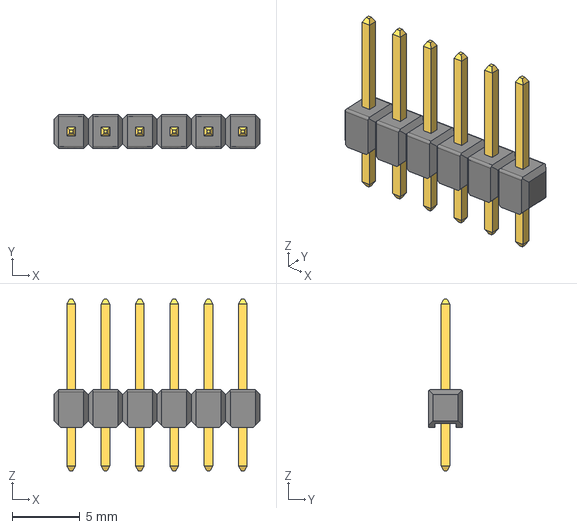
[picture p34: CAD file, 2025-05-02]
Processing_board/CAD models/PinHeaders/Pin Header 1x6 TH Pitch 2.54mm.stp
15.2 x 2.54 x 12.7 mm

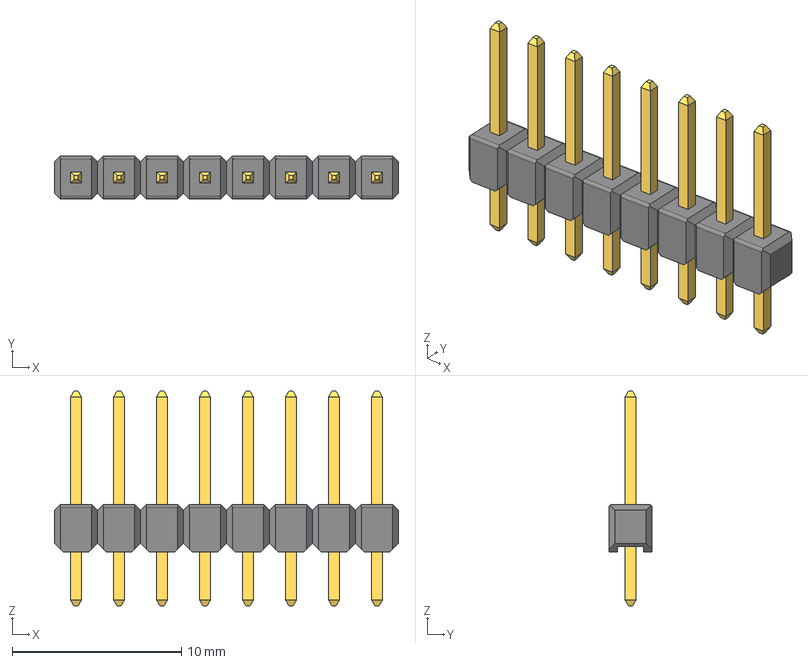
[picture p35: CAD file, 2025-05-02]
Processing_board/CAD models/PinHeaders/Pin Header 1x8 TH Pitch 2.54mm.stp
20.3 x 2.54 x 12.7 mm

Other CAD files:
Processing_board/CAD models/DLF162500LT-5028A1/DLF162500LT-5028A1.stp
Processing_board/CAD models/PinHeaders/Pin Header 1x3 TH Pitch 2.54mm.stp
Processing_board/Parts/DLF162500LT-5028A1/DLF162500LT-5028A1.stp

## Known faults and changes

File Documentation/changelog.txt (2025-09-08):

This file documents changes made to the board posterior to what is described in the Semester project report

(September 6-8)
commits c299b64830... and 3e60935701... corrected two errors described in the report (p22,
table 2) i.e. lack of 3V3 to VDDRF pin and incorrect wiring of both buttons
commit 
commit 9a5cc0a548 corrected the fact our exact model of STM32WBA63CIUX does NOT have an USART3 (mistake reading of the datasheet). The pins PA5 and PA7 are instead configured as GPIO, the silkscreen markings changed and they were rewired accordingly.(NB1 : the name of USART3 was already removed in the schematic before end of semester project, but the PCB footprint was not modified) (NB2 : R6 pullup resistor probably not useful anyore, should be removed)

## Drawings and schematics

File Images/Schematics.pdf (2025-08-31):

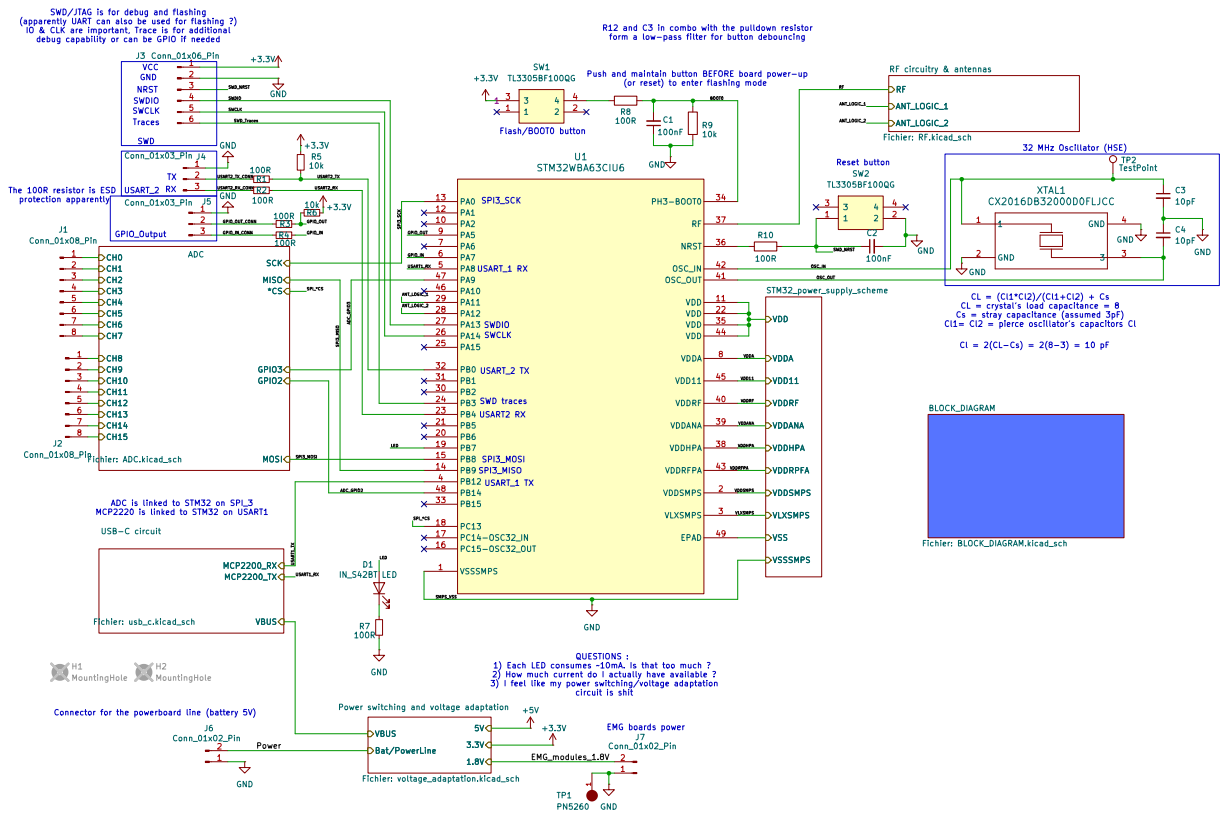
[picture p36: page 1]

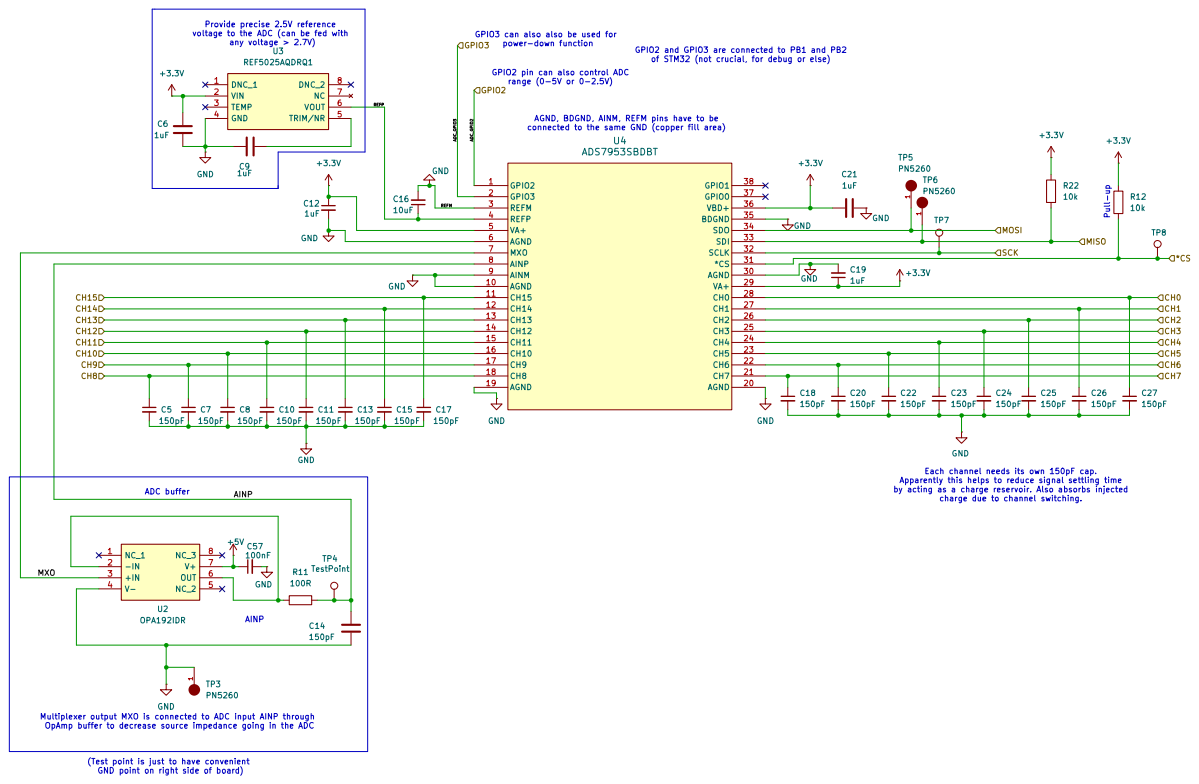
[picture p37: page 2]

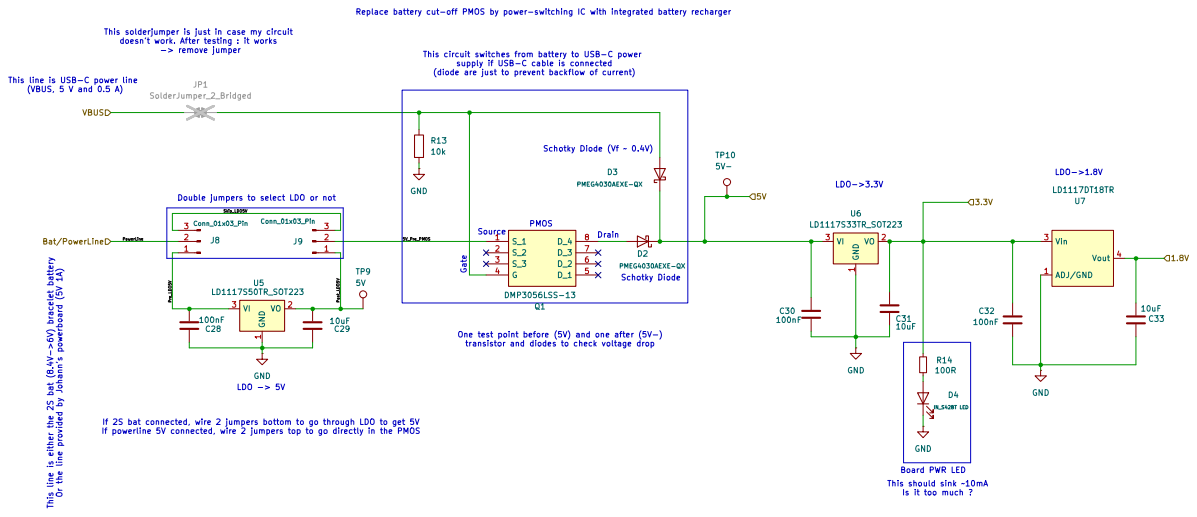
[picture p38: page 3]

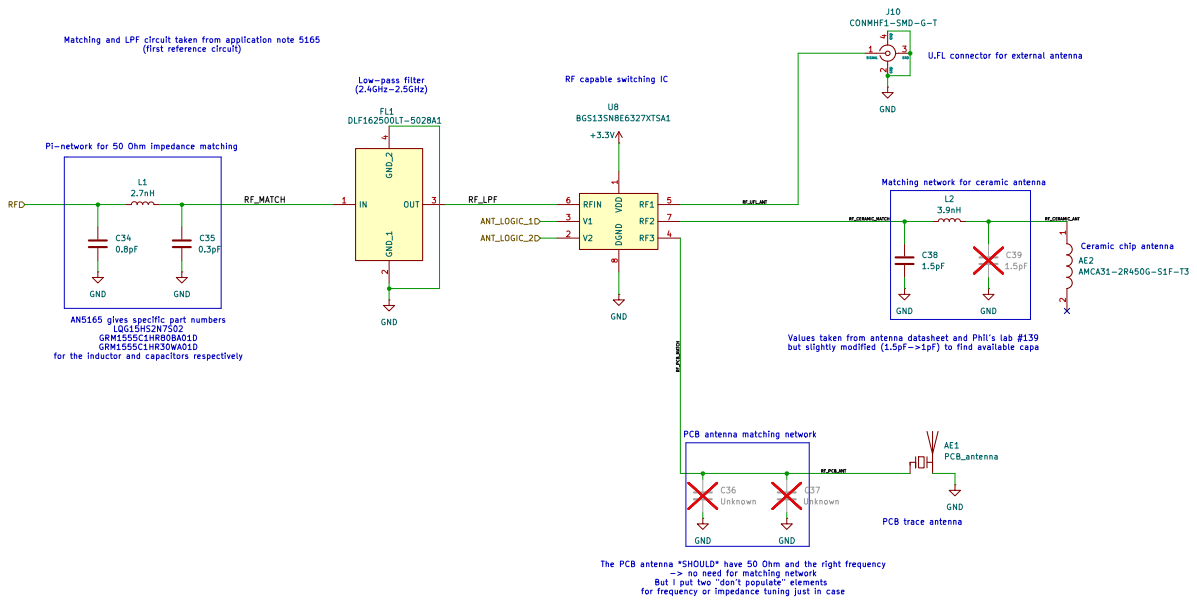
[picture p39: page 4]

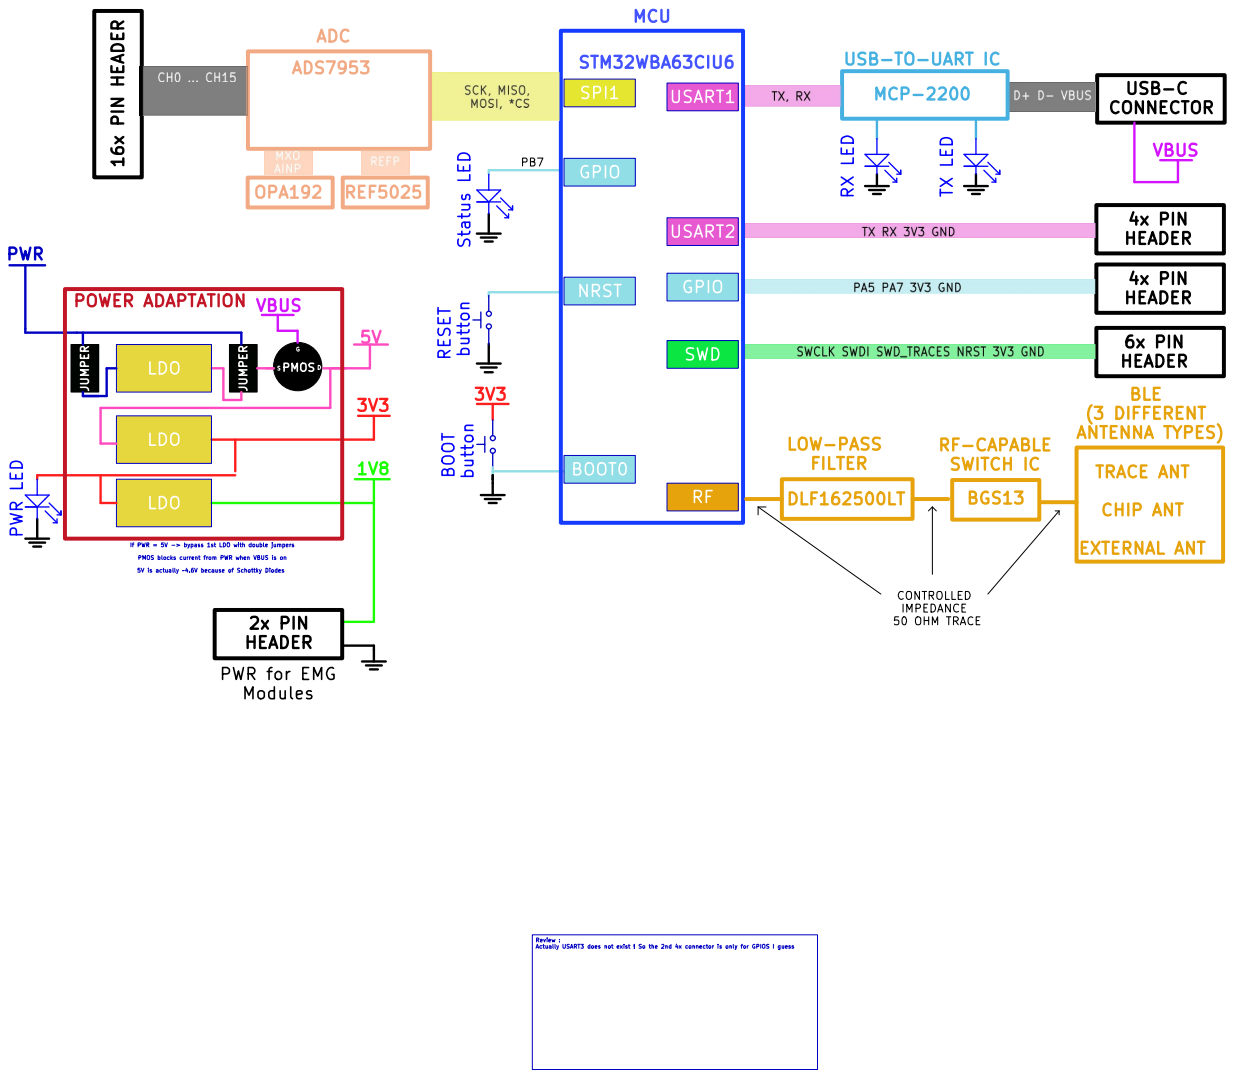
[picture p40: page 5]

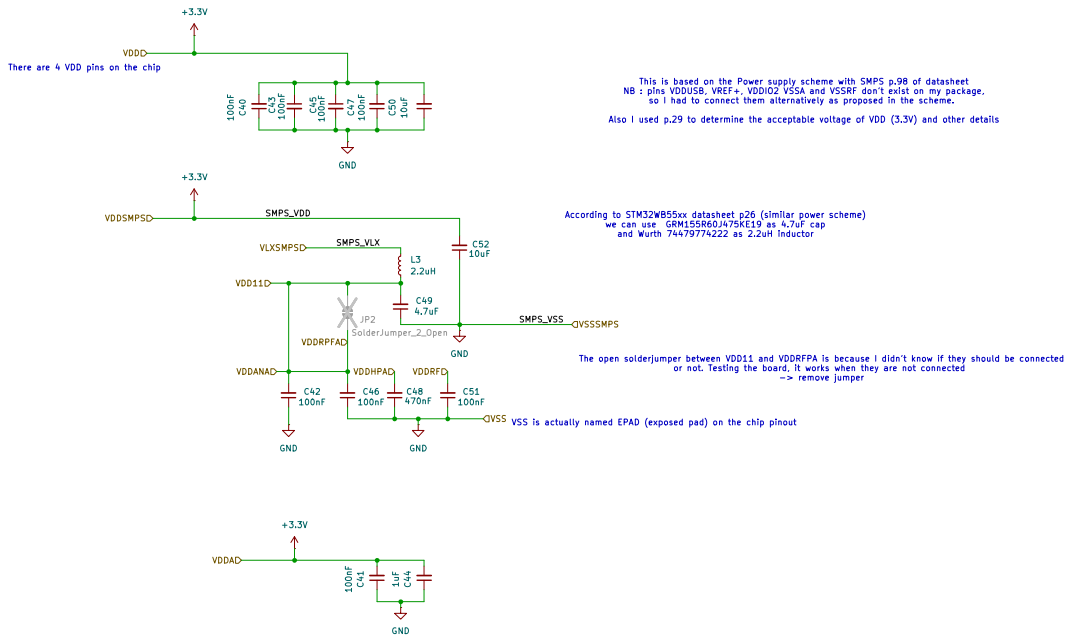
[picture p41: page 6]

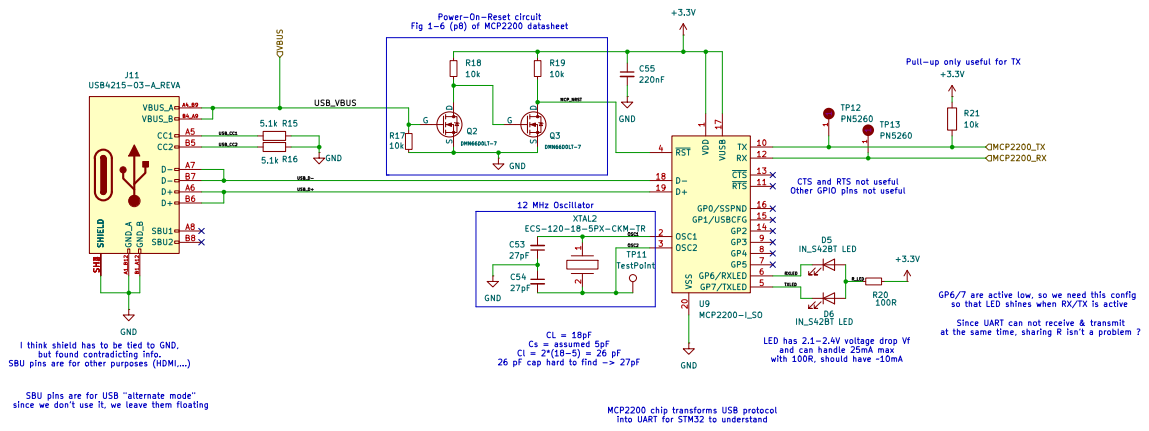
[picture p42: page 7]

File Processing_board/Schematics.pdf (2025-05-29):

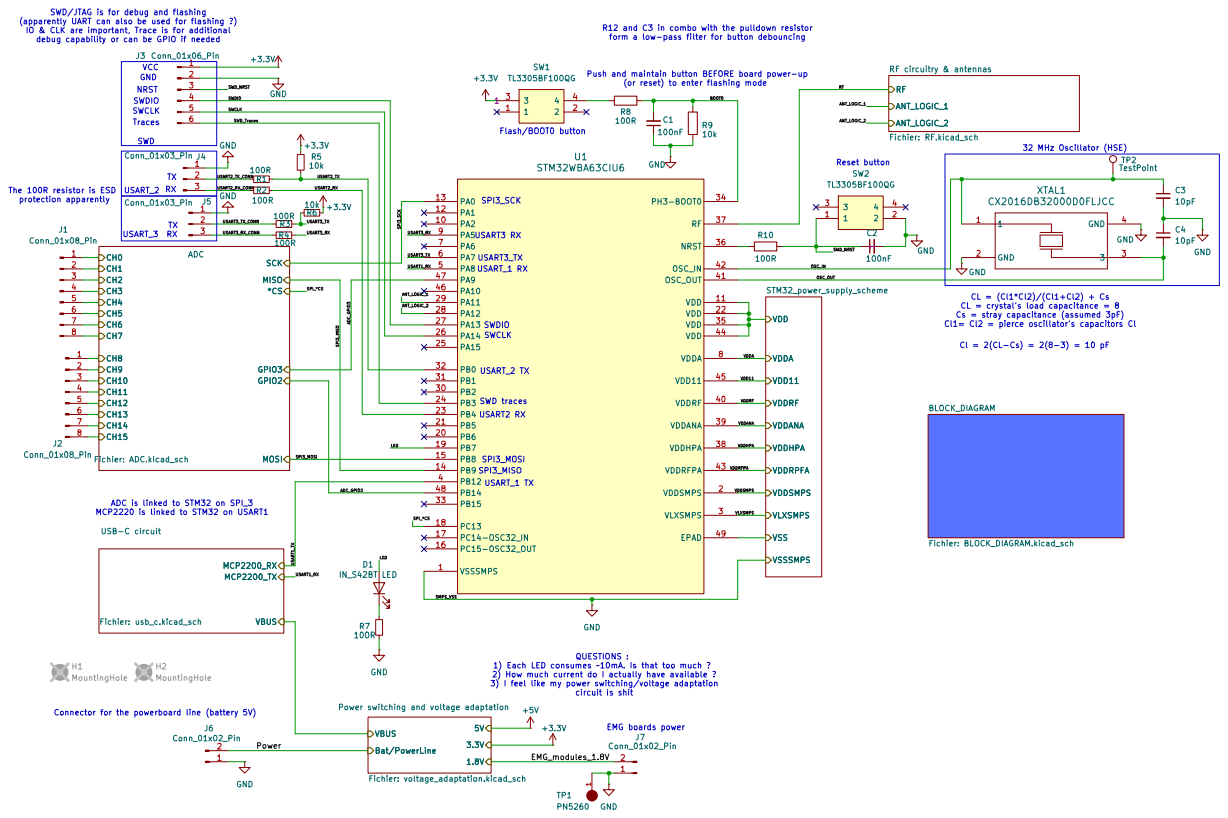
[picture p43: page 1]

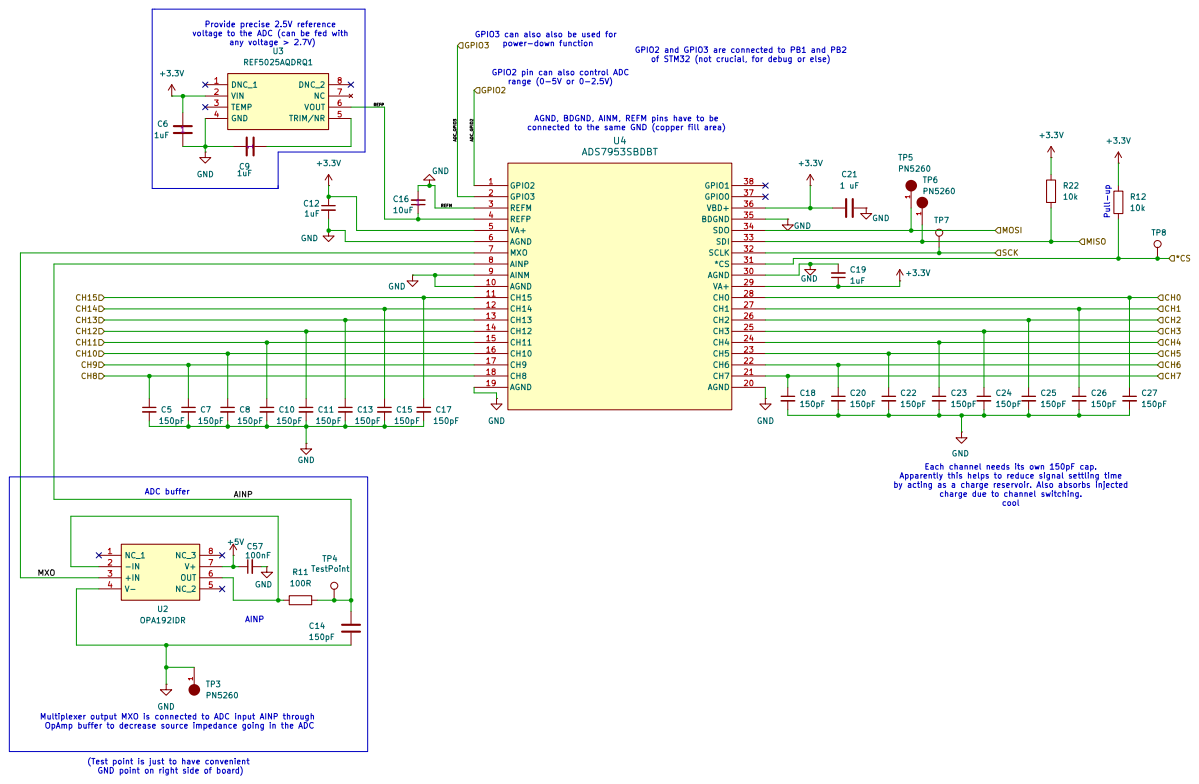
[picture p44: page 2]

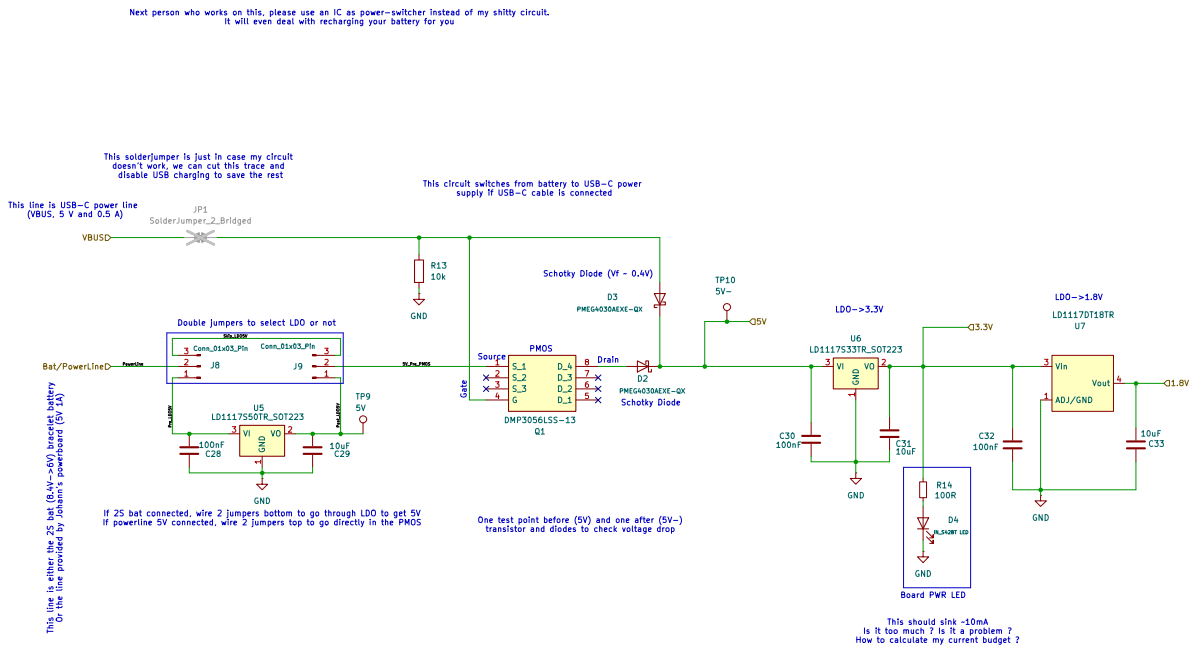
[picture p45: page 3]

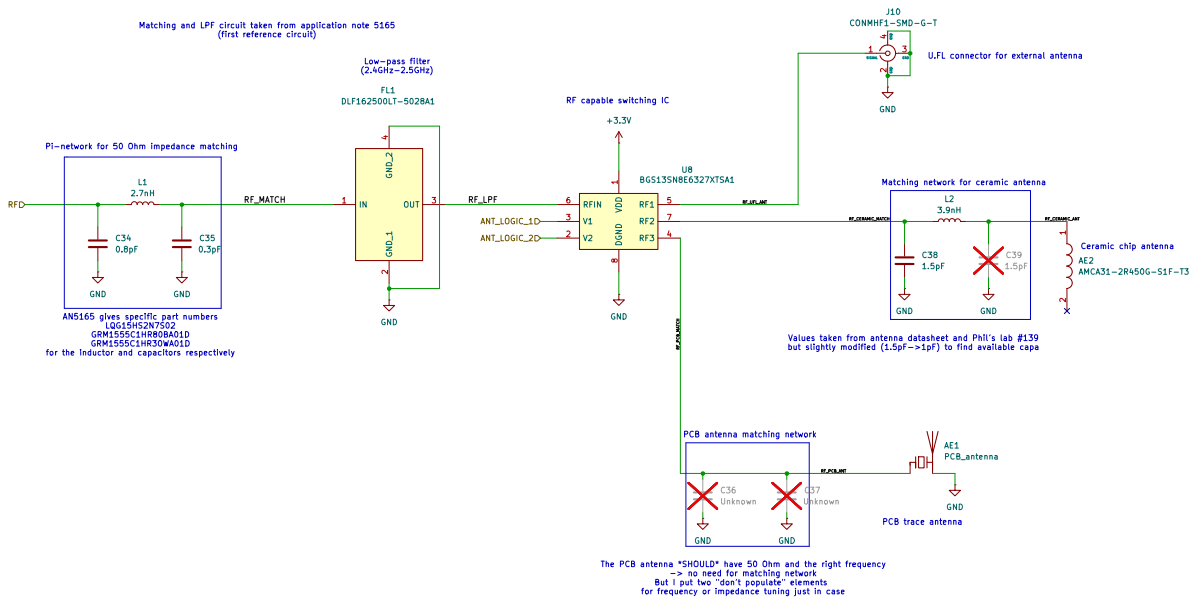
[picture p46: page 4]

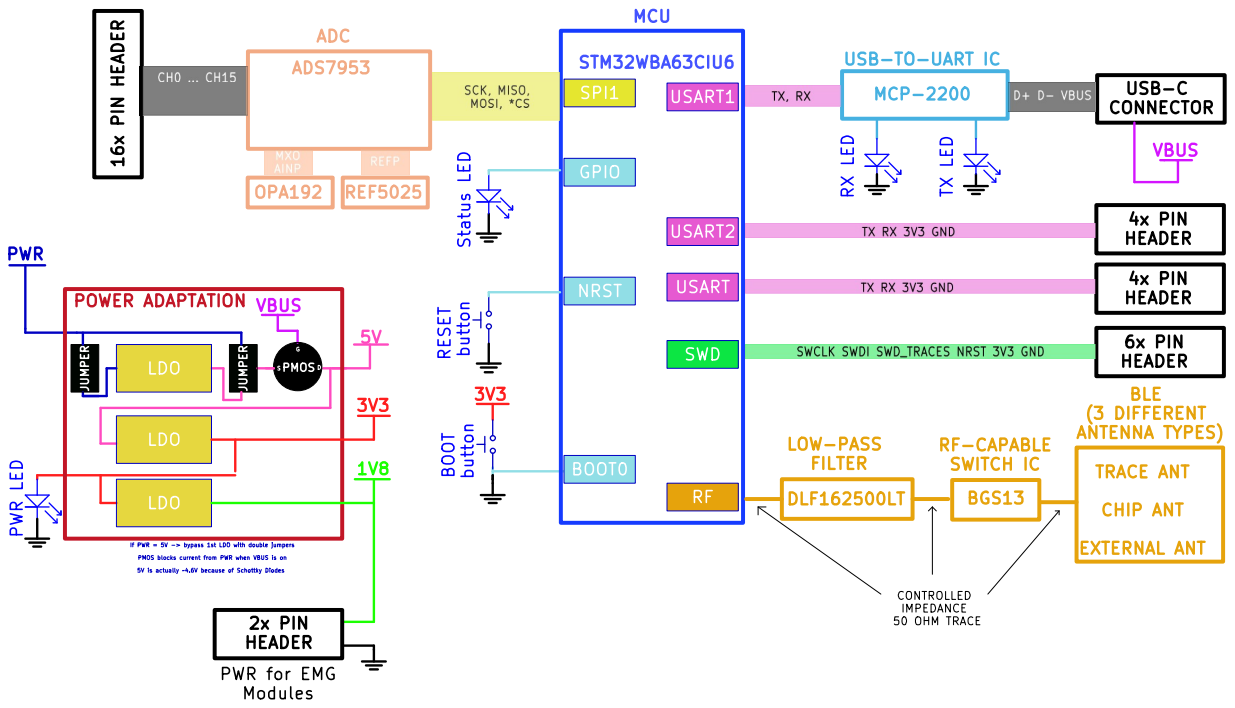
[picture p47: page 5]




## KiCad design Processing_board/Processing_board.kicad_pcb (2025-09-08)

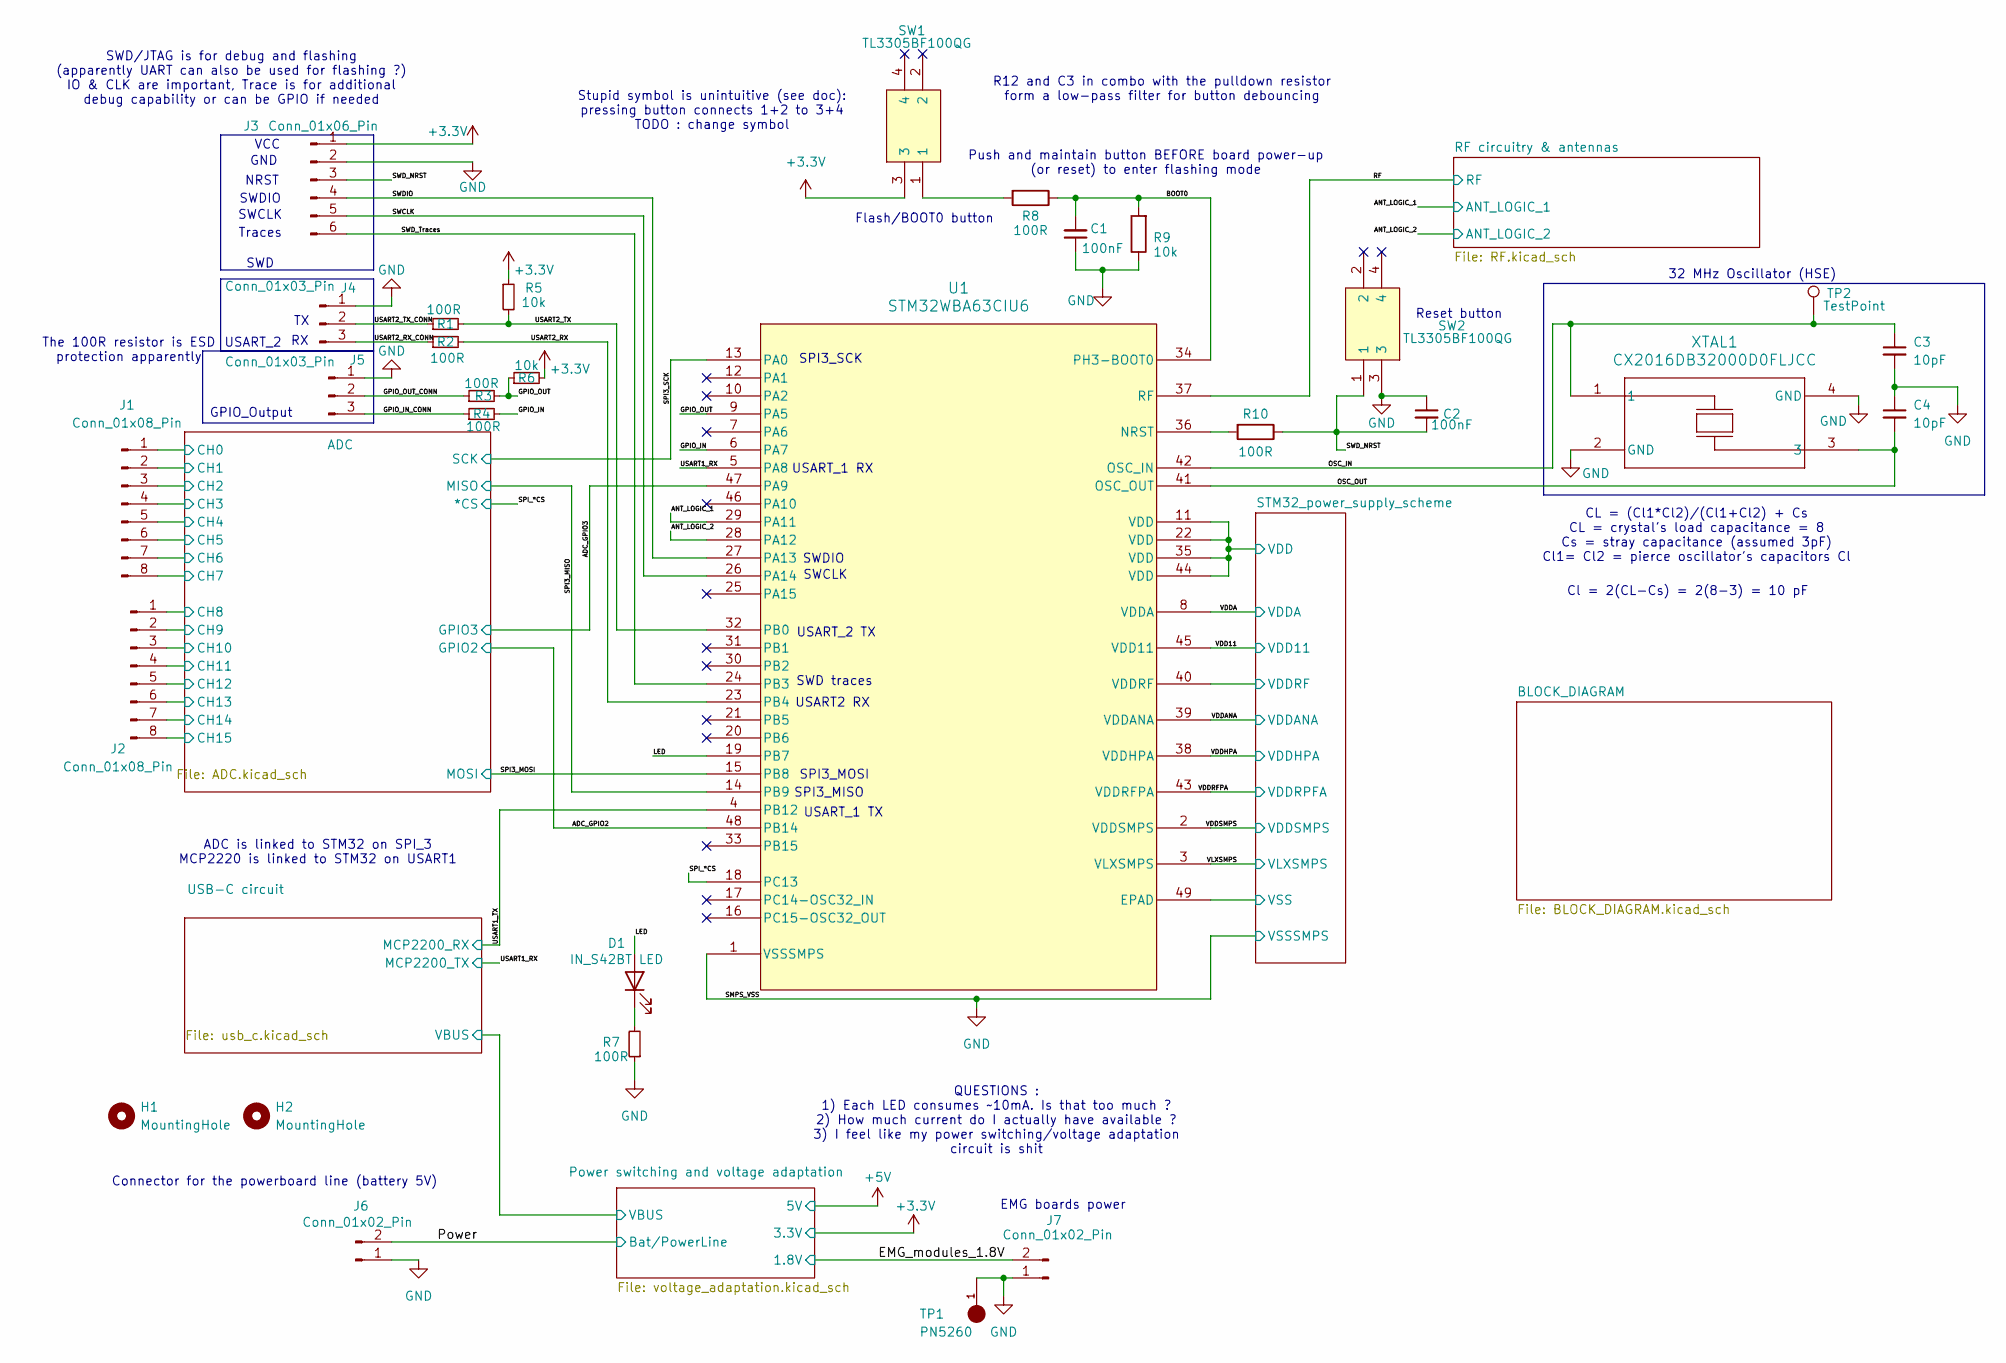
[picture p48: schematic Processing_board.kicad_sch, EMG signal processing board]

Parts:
C1, C2: 100nF; C_0402_1005Metric; Manufacturer_Part_Number CL05B104KP5VPNC
C3, C4: 10pF; C_0603_1608Metric; Manufacturer_Part_Number 0603ZC100KAT2A
D1: IN_S42BT LED; LED_0402_1005Metric; Manufacturer_Part_Number IN-S42BT5G
H1, H2: MountingHole; MountingHole_2.2mm_M2
J1, J2: Conn_01x08_Pin; PinSocket_1x08_P2.54mm_Vertical
J3: Conn_01x06_Pin; PinSocket_1x06_P2.54mm_Vertical
J4, J5: Conn_01x03_Pin; PinSocket_1x03_P2.54mm_Vertical
J6, J7: Conn_01x02_Pin; PinSocket_1x02_P2.54mm_Vertical
R1, R2, R3, R4, R7, R8, R10: 100R; R_0402_1005Metric; Manufacturer_Part_Number RK73B1ETTPD101J
R5, R6, R9: 10k; R_0402_1005Metric; Manufacturer_Part_Number 560112110020
SW1, SW2: TL3305BF100QG; TL3305BF160QG; Mouser Part Number 612-TL3305BF100QG
TP1: PN5260; Manufacturer_Part_Number 5260
TP2: TestPoint; TestPoint_Pad_D1.0mm
U1: STM32WBA63CIU6; UFQFPN-48_STM; Manufacturer_Part_Number STM32WBA63CIU6
XTAL1: CX2016DB32000D0FLJCC; xtal4_CX2016DB_AVX; Manufacturer_Part_Number CX2016DB32000D0FLJCC

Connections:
+3.3V: J3.1, R5.1, R6.2, SW1.3, U1.2 (VDDSMPS), U1.8 (VDDA), U1.11 (VDD), U1.22 (VDD), U1.35 (VDD), U1.40 (VDDRF), U1.44 (VDD); also elsewhere on the board
/ADC/CH0: J1.1; also elsewhere on the board
/ADC/CH1: J1.2; also elsewhere on the board
/ADC/CH2: J1.3; also elsewhere on the board
/ADC/CH3: J1.4; also elsewhere on the board
/ADC/CH4: J1.5; also elsewhere on the board
/ADC/CH5: J1.6; also elsewhere on the board
/ADC/CH6: J1.7; also elsewhere on the board
/ADC/CH7: J1.8; also elsewhere on the board
/ADC/CH8: J2.1; also elsewhere on the board
/ADC/CH9: J2.2; also elsewhere on the board
/ADC/CH10: J2.3; also elsewhere on the board
/ADC/CH11: J2.4; also elsewhere on the board
/ADC/CH12: J2.5; also elsewhere on the board
/ADC/CH13: J2.6; also elsewhere on the board
/ADC/CH14: J2.7; also elsewhere on the board
/ADC/CH15: J2.8; also elsewhere on the board
/ADC_GPIO2: U1.48 (PB14); also elsewhere on the board
/ADC_GPIO3: U1.47 (PA9); also elsewhere on the board
/ANT_LOGIC_1: U1.29 (PA11); also elsewhere on the board
/ANT_LOGIC_2: U1.28 (PA12); also elsewhere on the board
/BOOT0: C1.2, R8.1, R9.2, U1.34 (PH3-BOOT0)
/EMG_modules_1.8V: J7.2; also elsewhere on the board
/GPIO_IN: R4.2, U1.6 (PA7)
/GPIO_IN_CONN: J5.3, R4.1
/GPIO_OUT: R3.2, R6.1, U1.9 (PA5)
/GPIO_OUT_CONN: J5.2, R3.1
/LED: D1.2 (A), U1.19 (PB7)
/OSC_IN: C3.1, TP2.1, U1.42 (OSC_IN), XTAL1.1
/OSC_OUT: C4.2, U1.41 (OSC_OUT), XTAL1.3
/Power: J6.2; also elsewhere on the board
/RF: U1.37 (RF); also elsewhere on the board
/SPI3_MISO: U1.14 (PB9); also elsewhere on the board
/SPI3_MOSI: U1.15 (PB8); also elsewhere on the board
/SWCLK: J3.5, U1.26 (PA14)
/SWDIO: J3.4, U1.27 (PA13)
/SWD_NRST: C2.2, J3.3, R10.1, SW2.1
/SWD_Traces: J3.6, U1.24 (PB3)
/USART1_RX: U1.5 (PA8); also elsewhere on the board
/USART1_TX: U1.4 (PB12); also elsewhere on the board
/USART2_RX: R2.2, U1.23 (PB4)
/USART2_RX_CONN: J4.3, R2.1
/USART2_TX: R1.2, R5.2, U1.32 (PB0)
/USART2_TX_CONN: J4.2, R1.1
/VDD11: U1.39 (VDDANA), U1.43 (VDDRFPA), U1.45 (VDD11); also elsewhere on the board
/VDDHPA: U1.38 (VDDHPA); also elsewhere on the board
/VLXSMPS: U1.3 (VLXSMPS); also elsewhere on the board
unnamed: D1.1 (K), R7.2
unnamed: R8.2, SW1.1
unnamed: R10.2, U1.36 (NRST)

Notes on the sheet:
USART_1 TX
SWD/JTAG is for debug and flashing (apparently UART can also be used for flashing ?) IO & CLK are important, Trace is for additional debug capability or can be GPIO if needed
SWD
VCC
SPI3_MISO
The 100R resistor is ESD protection apparently
Reset button
32 MHz Oscillator (HSE)
SWCLK
SPI3_MOSI
EMG boards power
SPI3_SCK
Flash/BOOT0 button
CL = (Cl1*Cl2)/(Cl1+Cl2) + Cs CL = crystal's load capacitance = 8 Cs = stray capacitance (assumed 3pF) Cl1= Cl2 = pierce oscillator's capacitors Cl
Stupid symbol is unintuitive (see doc): pressing button connects 1+2 to 3+4 TODO : change symbol
Push and maintain button BEFORE board power-up (or reset) to enter flashing mode
NRST
SWDIO
ADC is linked to STM32 on SPI_3 MCP2220 is linked to STM32 on USART1
USART_2 TX
USART_2
Traces
USART_1 RX
GPIO_Output
QUESTIONS : 1) Each LED consumes ~10mA. Is that too much ? 2) How much current do I actually have available ? 3) I feel like my power switching/voltage adaptation circuit is shit
USART2 RX
Cl = 2(CL-Cs) = 2(8-3) = 10 pF
GND
R12 and C3 in combo with the pulldown resistor form a low-pass filter for button debouncing
Connector for the powerboard line (battery 5V)
SWD traces

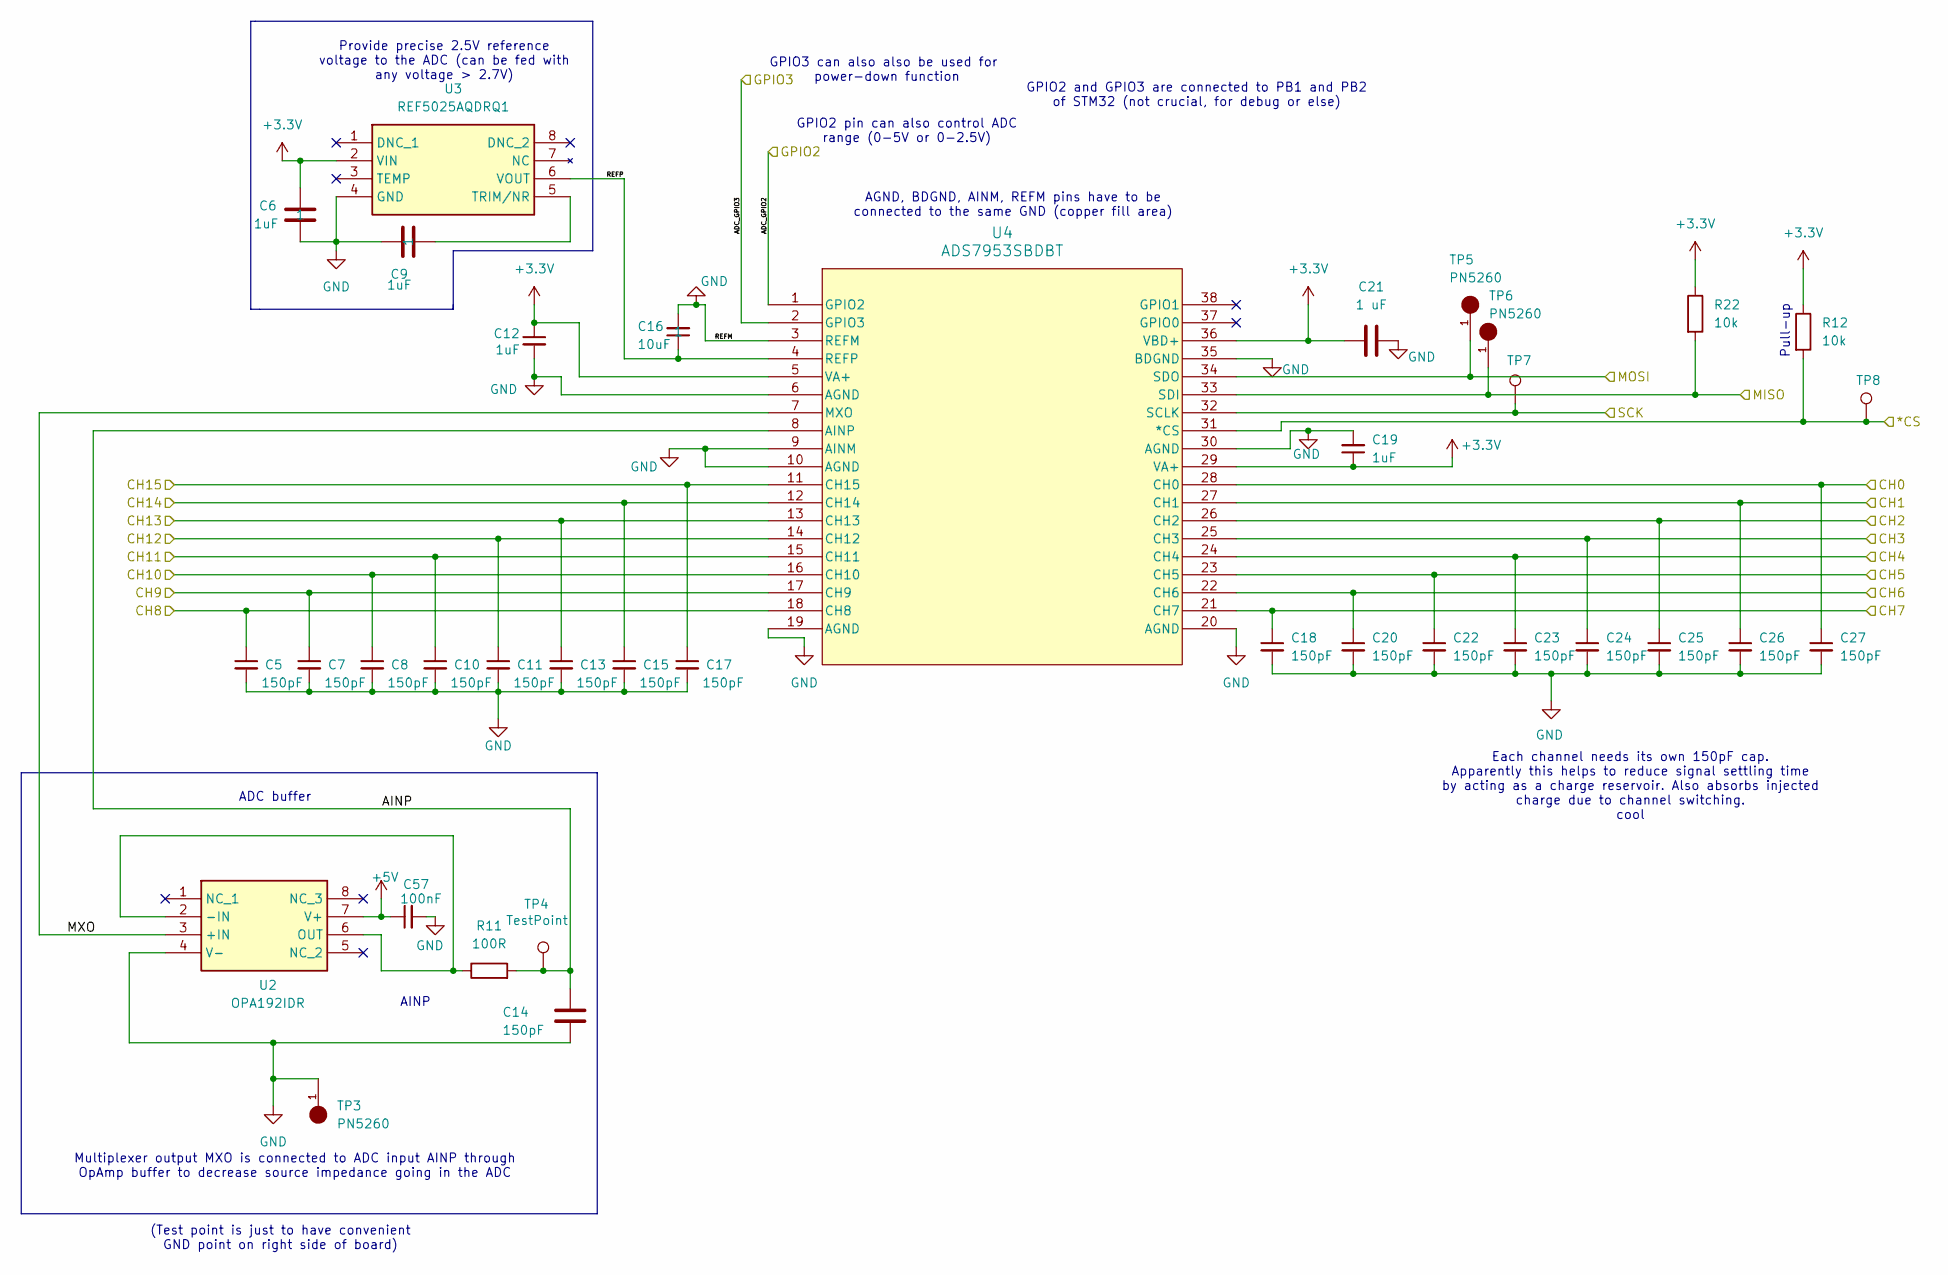
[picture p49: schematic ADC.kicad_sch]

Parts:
C5, C7, C8, C10, C11, C13, C14, C15, C17, C18, C20, C22, C23, C24, C25, C26, C27: 150pF; C_0402_1005Metric; Manufacturer_Part_Number C0402C151K5RACTU
C6, C9, C12, C19: 1uF; C_0402_1005Metric; Manufacturer_Part_Number CL05A105KP5NNNC
C16: 10uF; C_0402_1005Metric; Manufacturer_Part_Number GRM155R61A106ME11D
C21: 1 uF; C_0402_1005Metric; Manufacturer_Part_Number CL05A105KP5NNNC
C57: 100nF; C_0402_1005Metric; Manufacturer_Part_Number CL05B104KP5VPNC
R11: 100R; R_0402_1005Metric; Manufacturer_Part_Number RK73B1ETTPD101J
R12, R22: 10k; R_0402_1005Metric; Manufacturer_Part_Number 560112110020
TP3, TP5, TP6: PN5260; Manufacturer_Part_Number 5260
TP4, TP7, TP8: TestPoint; TestPoint_Pad_D1.0mm
U2: OPA192IDR; SOIC127P600X175-8N; Mouser Part Number 595-OPA192IDR
U3: REF5025AQDRQ1; SOIC127P600X175-8N; Mouser Part Number 595-REF5025AQDRQ1
U4: ADS7953SBDBT; DBT38; Manufacturer_Part_Number ADS7953SBDBT

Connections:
+3.3V: C6.1, C12.1, C19.1, C21.2, R12.1, R22.1, U3.2 (VIN), U4.5 (VA+), U4.29 (VA+), U4.36 (VBD+); also elsewhere on the board
+5V: C57.1, U2.7 (V+); also elsewhere on the board
/ADC/AINP: C14.1, R11.2, TP4.1, U4.8 (AINP)
/ADC/CH0: C27.1, U4.28 (CH0); also elsewhere on the board
/ADC/CH1: C26.1, U4.27 (CH1); also elsewhere on the board
/ADC/CH2: C25.1, U4.26 (CH2); also elsewhere on the board
/ADC/CH3: C24.1, U4.25 (CH3); also elsewhere on the board
/ADC/CH4: C23.1, U4.24 (CH4); also elsewhere on the board
/ADC/CH5: C22.1, U4.23 (CH5); also elsewhere on the board
/ADC/CH6: C20.1, U4.22 (CH6); also elsewhere on the board
/ADC/CH7: C18.1, U4.21 (CH7); also elsewhere on the board
/ADC/CH8: C5.1, U4.18 (CH8); also elsewhere on the board
/ADC/CH9: C7.1, U4.17 (CH9); also elsewhere on the board
/ADC/CH10: C8.1, U4.16 (CH10); also elsewhere on the board
/ADC/CH11: C10.1, U4.15 (CH11); also elsewhere on the board
/ADC/CH12: C11.1, U4.14 (CH12); also elsewhere on the board
/ADC/CH13: C13.1, U4.13 (CH13); also elsewhere on the board
/ADC/CH14: C15.1, U4.12 (CH14); also elsewhere on the board
/ADC/CH15: C17.1, U4.11 (CH15); also elsewhere on the board
/ADC/MXO: U2.3 (+IN), U4.7 (MXO)
/ADC/REFP: C16.1, U3.6 (VOUT), U4.4 (REFP)
/ADC_GPIO2: U4.1 (GPIO2); also elsewhere on the board
/ADC_GPIO3: U4.2 (GPIO3); also elsewhere on the board
/SPI3_MISO: R22.2, TP6.1, U4.33 (SDI); also elsewhere on the board
/SPI3_MOSI: TP5.1, U4.34 (SDO); also elsewhere on the board
unnamed: R11.1, U2.2 (-IN), U2.6 (OUT)
unnamed: C9.2, U3.5 (TRIM/NR)

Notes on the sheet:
AGND, BDGND, AINM, REFM pins have to be connected to the same GND (copper fill area)
ADC buffer
Provide precise 2.5V reference voltage to the ADC (can be fed with any voltage > 2.7V)
GPIO3 can also also be used for power-down function
Multiplexer output MXO is connected to ADC input AINP through OpAmp buffer to decrease source impedance going in the ADC
Each channel needs its own 150pF cap. Apparently this helps to reduce signal settling time by acting as a charge reservoir. Also absorbs injected charge due to channel switching. cool
GPIO2 and GPIO3 are connected to PB1 and PB2 of STM32 (not crucial, for debug or else)
AINP
Pull-up
GPIO2 pin can also control ADC range (0-5V or 0-2.5V)
(Test point is just to have convenient GND point on right side of board)

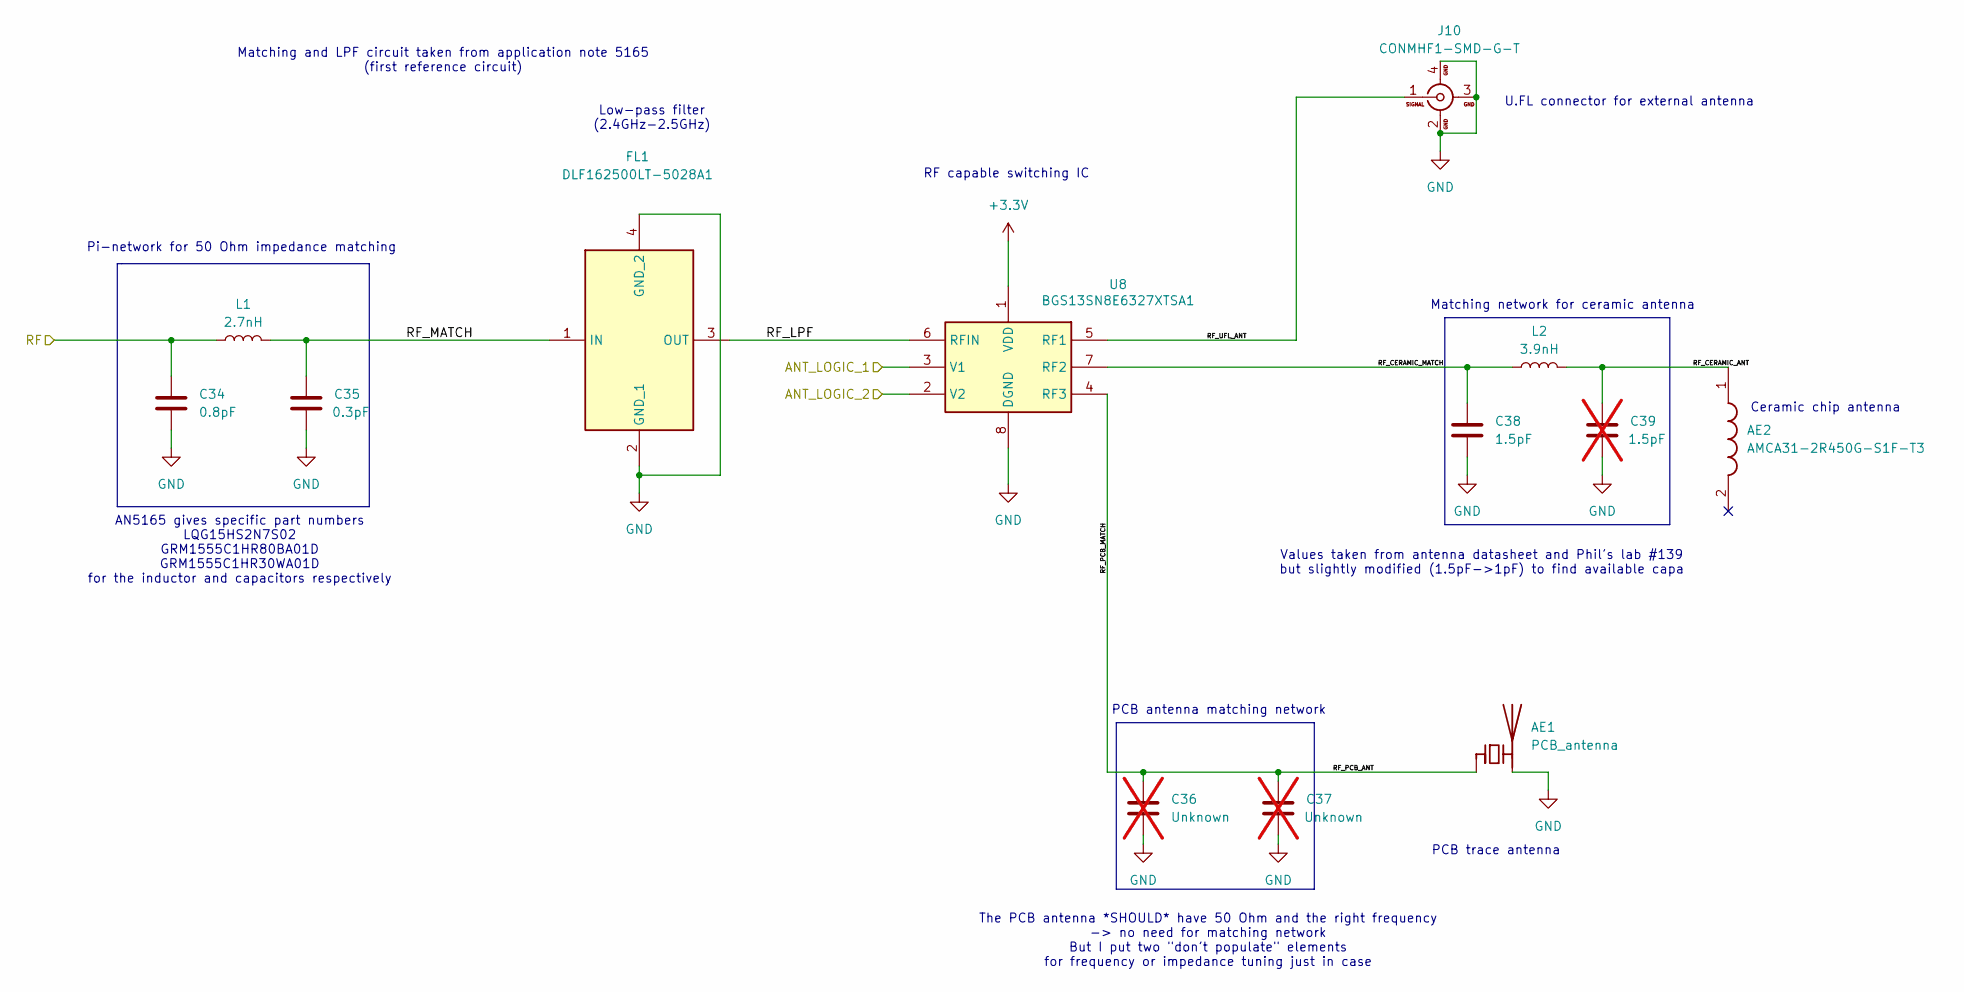
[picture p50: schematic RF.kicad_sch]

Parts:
AE1: PCB_antenna; Texas_SWRA117D_2.4GHz_Left
AE2: AMCA31-2R450G-S1F-T3; ANTC3216X140N; Mouser Part Number 815-CA312R450GS1FT3
C34: 0.8pF; C_0402_1005Metric; Manufacturer_Part_Number GRM1555C1HR80BA01D
C35: 0.3pF; C_0402_1005Metric; Manufacturer_Part_Number GRM1555C1HR30WA01D
C36, C37: Unknown; C_0402_1005Metric; not fitted
C38: 1.5pF; C_0402_1005Metric; Manufacturer_Part_Number 0402N1R5B100CT
C39: 1.5pF; C_0402_1005Metric; not fitted
FL1: DLF162500LT-5028A1; DLF162500LT5028A1; Mouser Part Number 810-DLF16250LT5028A1
J10: CONMHF1-SMD-G-T; CONMHF1SMDGT; Mouser Part Number 712-CONMHF1-SMD-G-T
L1: 2.7nH; L_0402_1005Metric; Manufacturer_Part_Number LQG15HS2N7S02D
L2: 3.9nH; L_0402_1005Metric; Manufacturer_Part_Number 36550402S3N9T
U8: BGS13SN8E6327XTSA1; Mouser Part Number 726-BGS13SN8E6327XTS

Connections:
+3.3V: U8.1 (VDD); also elsewhere on the board
/ANT_LOGIC_1: U8.3 (V1); also elsewhere on the board
/ANT_LOGIC_2: U8.2 (V2); also elsewhere on the board
/RF: C34.1, L1.1; also elsewhere on the board
/RF circuitry & antennas/RF_CERAMIC_MATCH: C38.1, L2.1, U8.7 (RF2)
/RF circuitry & antennas/RF_LPF: FL1.3 (OUT), U8.6 (RFIN)
/RF circuitry & antennas/RF_MATCH: C35.1, FL1.1 (IN), L1.2
/RF circuitry & antennas/RF_PCB_ANT: AE1.1 (FEED), C36.1, C37.1, U8.4 (RF3)
/RF circuitry & antennas/RF_UFL_ANT: J10.1, U8.5 (RF1)

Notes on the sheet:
The PCB antenna *SHOULD* have 50 Ohm and the right frequency -> no need for matching network But I put two "don't populate" elements for frequency or impedance tuning just in case
U.FL connector for external antenna
RF capable switching IC
Pi-network for 50 Ohm impedance matching
Matching and LPF circuit taken from application note 5165 (first reference circuit)
AN5165 gives specific part numbers LQG15HS2N7S02 GRM1555C1HR80BA01D GRM1555C1HR30WA01D for the inductor and capacitors respectively
Ceramic chip antenna
PCB trace antenna
Low-pass filter (2.4GHz-2.5GHz)
PCB antenna matching network
Values taken from antenna datasheet and Phil's lab #139 but slightly modified (1.5pF->1pF) to find available capa
Matching network for ceramic antenna

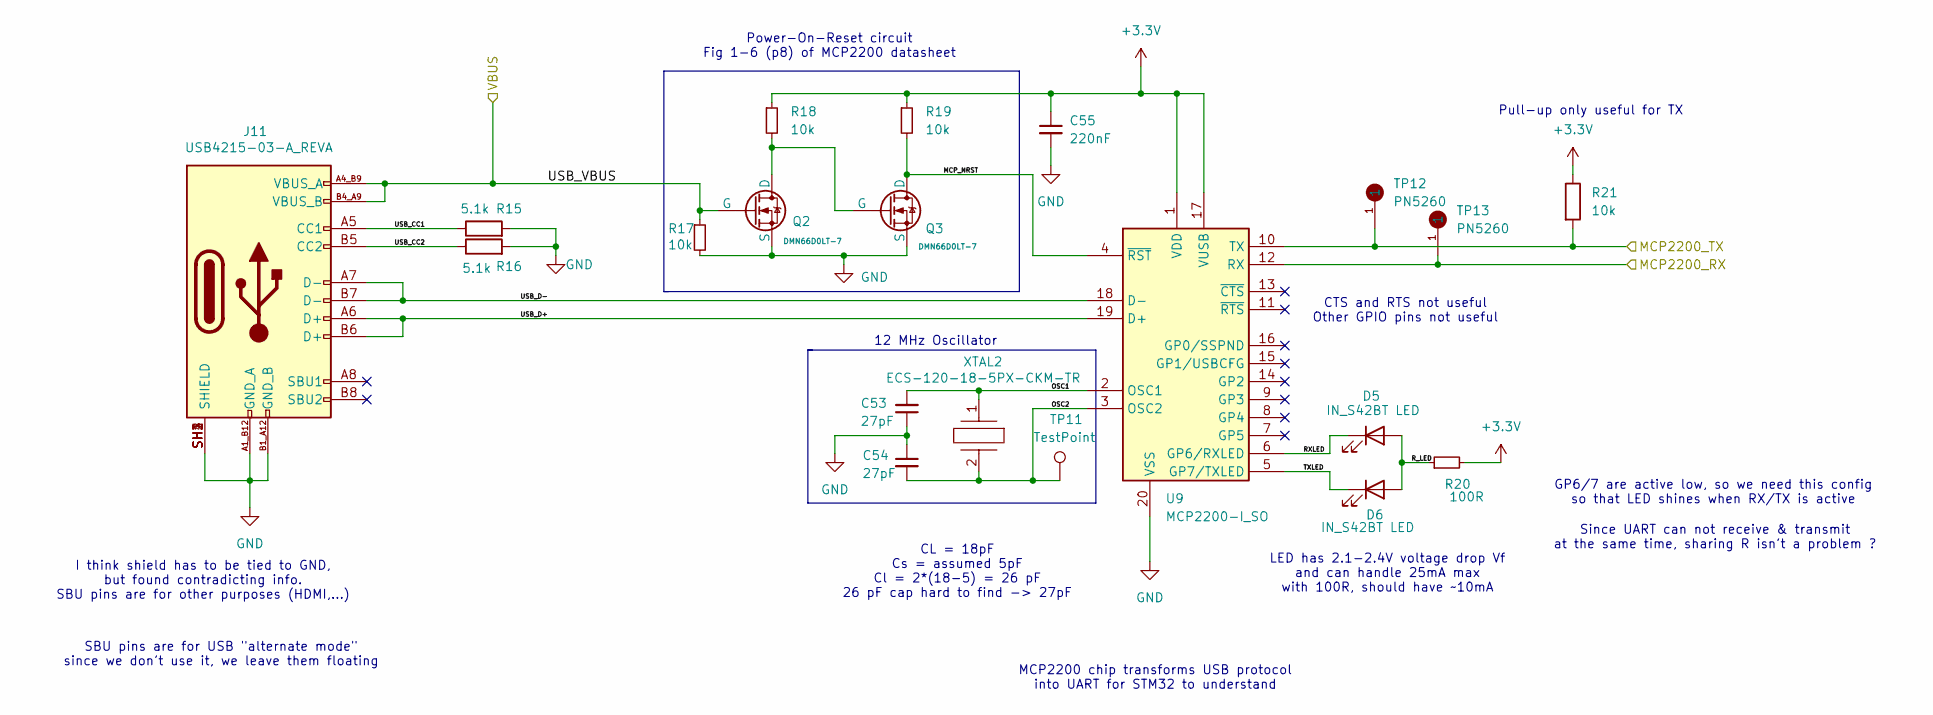
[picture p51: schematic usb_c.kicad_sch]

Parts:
C53, C54: 27pF; C_0805_2012Metric; Manufacturer_Part_Number 08055C270KAT2A
C55: 220nF; C_0402_1005Metric; Manufacturer_Part_Number GRT155R71A224KE01D
D5, D6: IN_S42BT LED; LED_0402_1005Metric; Manufacturer_Part_Number IN-S42BT5G
J11: USB4215-03-A_REVA; GCT_USB4215-03-A_REVA; PARTREV A
Q2, Q3: DMN66D0LT-7; SOT50P160X90-3N; Mouser Part Number 621-DMN66D0LT-7
R15, R16: 5.1k; R_0402_1005Metric; Manufacturer_Part_Number AC0402JR-075K1L
R17, R18, R19, R21: 10k; R_0402_1005Metric; Manufacturer_Part_Number 560112110020
R20: 100R; R_0402_1005Metric; Manufacturer_Part_Number RK73B1ETTPD101J
TP11: TestPoint; TestPoint_Pad_D1.0mm
TP12, TP13: PN5260; Manufacturer_Part_Number 5260
U9: MCP2200-I_SO; SOIC127P1030X265-20N; Mouser Part Number 579-MCP2200-I/SO
XTAL2: ECS-120-18-5PX-CKM-TR; ECS120185PXCKMTR; Mouser Part Number 520-ECS120185PXCKMTR

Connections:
+3.3V: C55.1, R18.1, R19.1, R20.2, R21.1, U9.1 (VDD), U9.17 (VUSB); also elsewhere on the board
/USART1_RX: R21.2, TP12.1, U9.10 (TX); also elsewhere on the board
/USART1_TX: TP13.1, U9.12 (RX); also elsewhere on the board
/USB-C circuit/MCP_NRST: Q3.1 (D), R19.2, U9.4 (~RST)
/USB-C circuit/OSC1: C53.2, U9.2 (OSC1), XTAL2.1
/USB-C circuit/OSC2: C54.2, TP11.1, U9.3 (OSC2), XTAL2.2
/USB-C circuit/RXLED: D5.1 (K), U9.6 (GP6/RXLED)
/USB-C circuit/R_LED: D5.2 (A), D6.2 (A), R20.1
/USB-C circuit/TXLED: D6.1 (K), U9.5 (GP7/TXLED)
/USB-C circuit/USB_CC1: J11.A5 (CC1), R15.1
/USB-C circuit/USB_CC2: J11.B5 (CC2), R16.1
/USB-C circuit/USB_D+: J11.A6 (D+), J11.B6 (D+), U9.19 (D+)
/USB-C circuit/USB_D-: J11.A7 (D-), J11.B7 (D-), U9.18 (D-)
/USB-C circuit/USB_VBUS: J11.A4_B9 (VBUS_A), J11.B4_A9 (VBUS_B), Q2.2 (G), R17.1; also elsewhere on the board
unnamed: Q2.1 (D), Q3.2 (G), R18.2

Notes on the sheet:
Power-On-Reset circuit Fig 1-6 (p8) of MCP2200 datasheet
I think shield has to be tied to GND, but found contradicting info. SBU pins are for other purposes (HDMI,...)
Since UART can not receive & transmit at the same time, sharing R isn't a problem ?
GP6/7 are active low, so we need this config so that LED shines when RX/TX is active
LED has 2.1-2.4V voltage drop Vf and can handle 25mA max with 100R, should have ~10mA
SBU pins are for USB "alternate mode" since we don't use it, we leave them floating
Pull-up only useful for TX
CL = 18pF Cs = assumed 5pF Cl = 2*(18-5) = 26 pF 26 pF cap hard to find -> 27pF
12 MHz Oscillator
MCP2200 chip transforms USB protocol into UART for STM32 to understand
CTS and RTS not useful Other GPIO pins not useful

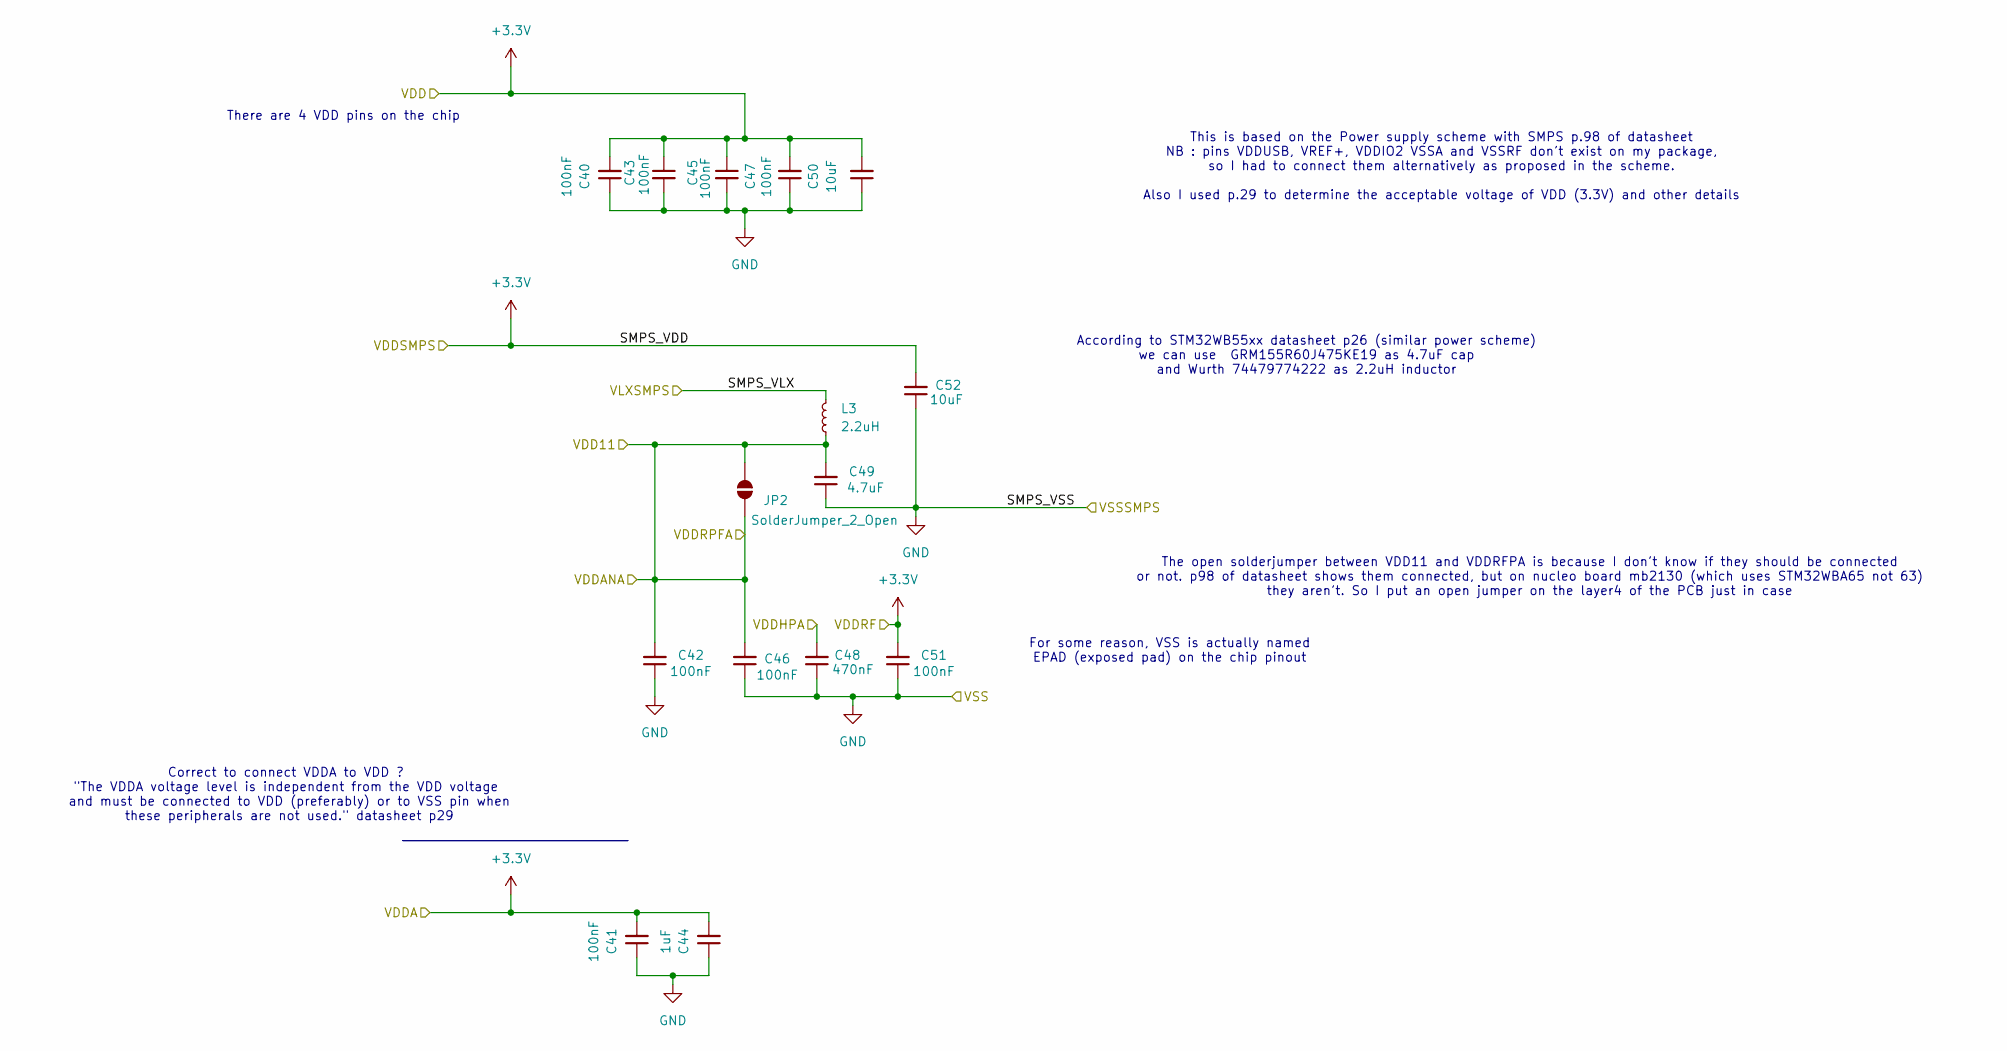
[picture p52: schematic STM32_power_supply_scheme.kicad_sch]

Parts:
C40, C41, C42, C43, C45, C46, C47, C51: 100nF; C_0402_1005Metric; Manufacturer_Part_Number CL05B104KP5VPNC
C44: 1uF; C_0402_1005Metric; Manufacturer_Part_Number CL05A105KP5NNNC
C48: 470nF; C_0402_1005Metric; Manufacturer_Part_Number C0402C473K8RACAUTO7411
C49: 4.7uF; C_0402_1005Metric; Manufacturer_Part_Number GRM155C61E475ME15D
C50, C52: 10uF; C_0402_1005Metric; Manufacturer_Part_Number GRM155R61A106ME11D
JP2: SolderJumper_2_Open; SolderJumper-2_P1.3mm_Open_RoundedPad1.0x1.5mm
L3: 2.2uH; L_0805_2012Metric; Manufacturer_Part_Number 74479774222

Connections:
+3.3V: C40.2, C41.2, C43.1, C44.2, C45.1, C47.2, C50.2, C51.2, C52.2; also elsewhere on the board
/VDD11: C42.2, C46.2, C49.2, JP2.1 (A), JP2.2 (B), L3.1; also elsewhere on the board
/VDDHPA: C48.2; also elsewhere on the board
/VLXSMPS: L3.2; also elsewhere on the board

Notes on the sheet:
Correct to connect VDDA to VDD ? "The VDDA voltage level is independent from the VDD voltage and must be connected to VDD (preferably) or to VSS pin when these peripherals are not used." datasheet p29
There are 4 VDD pins on the chip
The open solderjumper between VDD11 and VDDRFPA is because I don't know if they should be connected or not. p98 of datasheet shows them connected, but on nucleo board mb2130 (which uses STM32WBA65 not 63) they aren't. So I put an open jumper on the layer4 of the PCB just in case
This is based on the Power supply scheme with SMPS p.98 of datasheet NB : pins VDDUSB, VREF+, VDDIO2 VSSA and VSSRF don't exist on my package, so I had to connect them alternatively as proposed in the scheme. Also I used p.29 to determine the acceptable voltage of VDD (3.3V) and other details
According to STM32WB55xx datasheet p26 (similar power scheme) we can use GRM155R60J475KE19 as 4.7uF cap and Wurth 74479774222 as 2.2uH inductor
For some reason, VSS is actually named EPAD (exposed pad) on the chip pinout

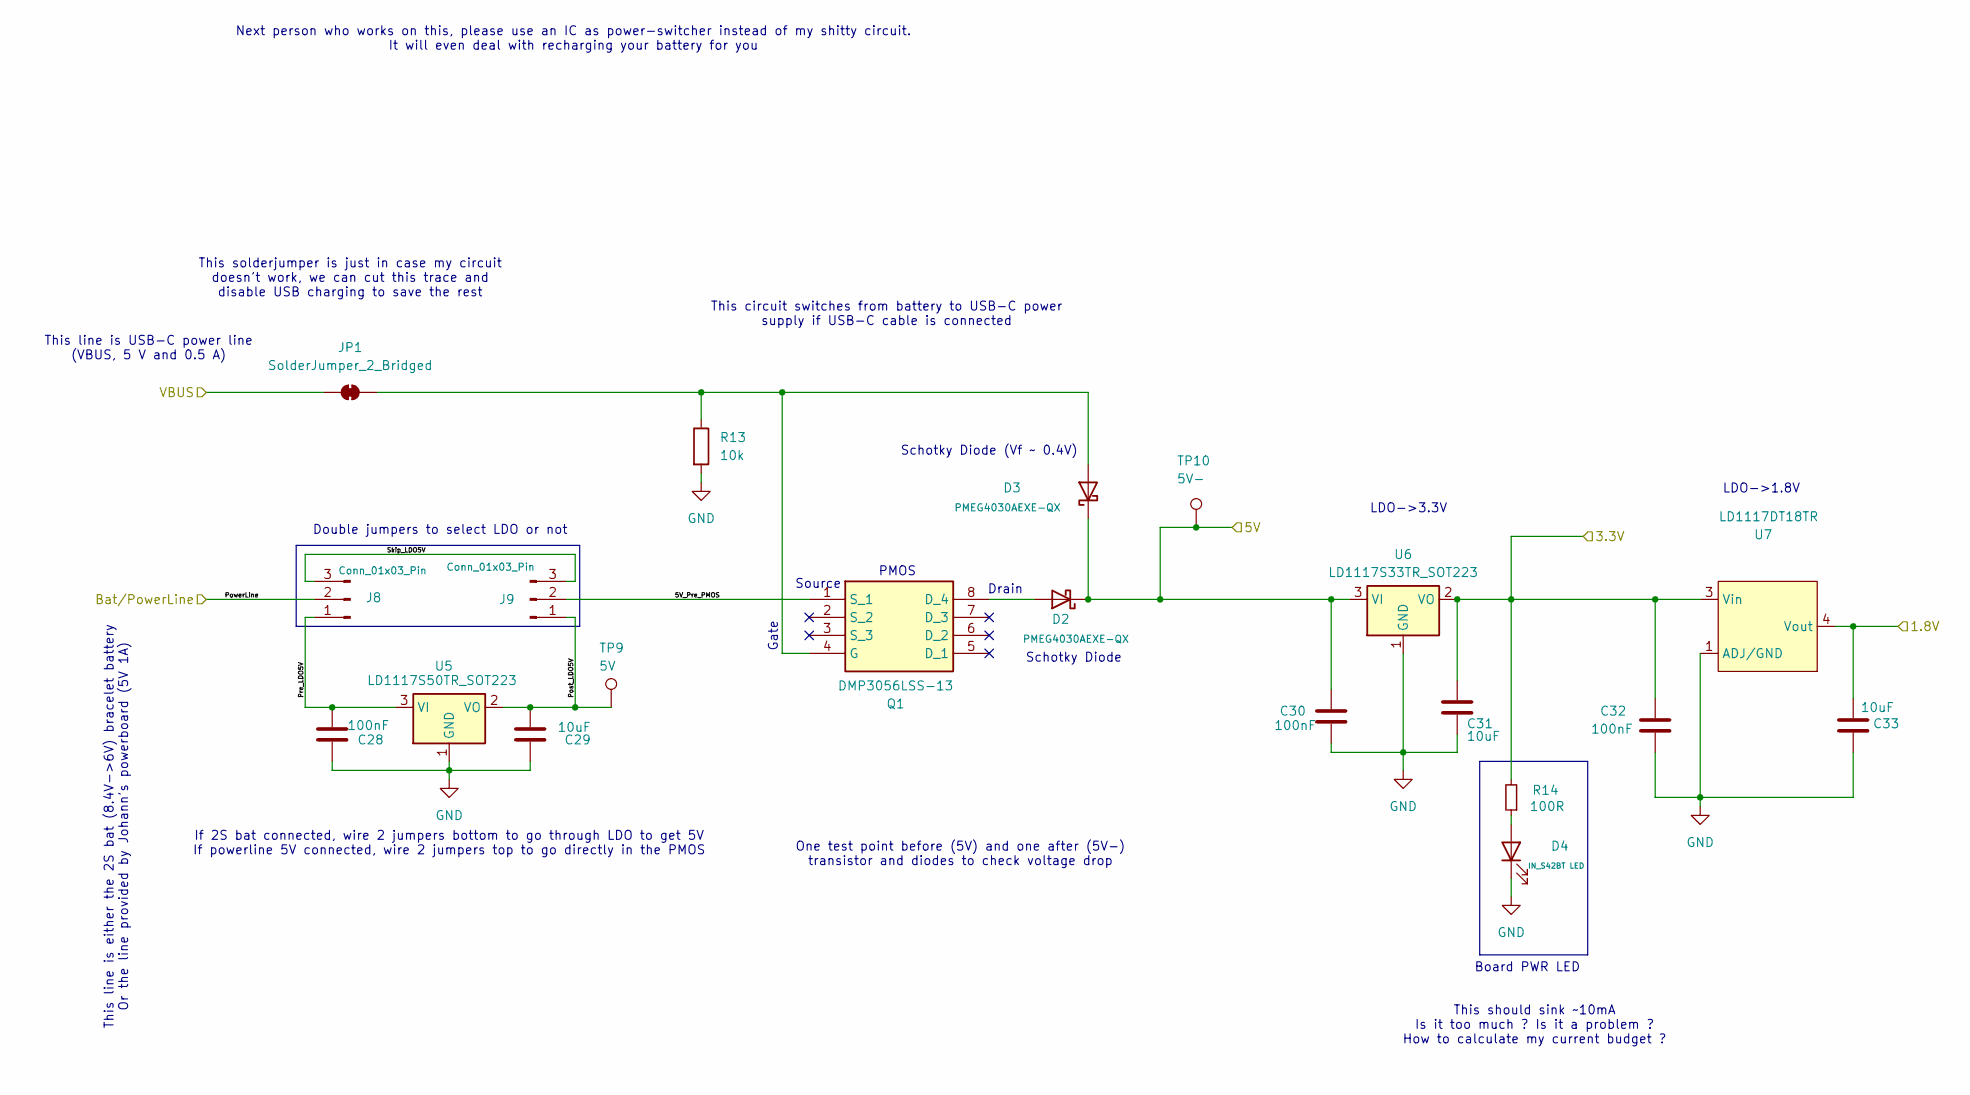
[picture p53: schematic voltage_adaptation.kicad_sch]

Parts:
C28, C30, C32: 100nF; C_0402_1005Metric; Manufacturer_Part_Number CL05B104KP5VPNC
C29, C31, C33: 10uF; C_0402_1005Metric; Manufacturer_Part_Number GRM155R61A106ME11D
D2, D3: PMEG4030AEXE-QX; PMEG4030AEXEQX; Manufacturer_Part_Number PMEG4030AEXE-QX
D4: IN_S42BT LED; LED_0402_1005Metric; Manufacturer_Part_Number IN-S42BT5G
J8, J9: Conn_01x03_Pin; PinSocket_1x03_P2.54mm_Vertical
JP1: SolderJumper_2_Bridged; SolderJumper-2_P1.3mm_Bridged2Bar_RoundedPad1.0x1.5mm
Q1: DMP3056LSS-13; SOIC127P600X170-8N; Mouser Part Number 621-DMP3056LSS-13
R13: 10k; R_0402_1005Metric; Manufacturer_Part_Number 560112110020
R14: 100R; R_0402_1005Metric; Manufacturer_Part_Number RK73B1ETTPD101J
TP9: 5V; TestPoint_Pad_D1.0mm
TP10: 5V-; TestPoint_Pad_D1.0mm
U5: LD1117S50TR_SOT223; SOT-223-3_TabPin2; Manufacturer_Part_Number LD1117S50TR
U6: LD1117S33TR_SOT223; SOT-223-3_TabPin2; Manufacturer_Part_Number LD1117S33TR
U7: LD1117DT18TR; TO228P972X240-3N; Manufacturer_Part_Number LD1117DT18TR

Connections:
+3.3V: C31.1, C32.1, R14.2, U6.2 (VO), U7.3 (Vin); also elsewhere on the board
+5V: C30.1, D2.1 (K), D2.3 (K), D3.1 (K), D3.3 (K), TP10.1, U6.3 (VI); also elsewhere on the board
/EMG_modules_1.8V: C33.2, U7.4 (Vout); also elsewhere on the board
/Power: J8.2; also elsewhere on the board
/Power switching and voltage adaptation/5V_Pre_PMOS: J9.2, Q1.1 (S_1)
/Power switching and voltage adaptation/Post_LDO5V: C29.2, J9.1, TP9.1, U5.2 (VO)
/Power switching and voltage adaptation/Pre_LDO5V: C28.2, J8.1, U5.3 (VI)
/Power switching and voltage adaptation/Skip_LDO5V: J8.3, J9.3
/USB-C circuit/USB_VBUS: JP1.1 (A); also elsewhere on the board
unnamed: D2.2 (A), Q1.8 (D_4)
unnamed: D3.2 (A), JP1.2 (B), Q1.4 (G), R13.1
unnamed: D4.2 (A), R14.1

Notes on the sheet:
LDO->3.3V
If 2S bat connected, wire 2 jumpers bottom to go through LDO to get 5V If powerline 5V connected, wire 2 jumpers top to go directly in the PMOS
Double jumpers to select LDO or not
Next person who works on this, please use an IC as power-switcher instead of my shitty circuit. It will even deal with recharging your battery for you
This should sink ~10mA Is it too much ? Is it a problem ? How to calculate my current budget ?
Drain
Schotky Diode (Vf ~ 0.4V)
One test point before (5V) and one after (5V-) transistor and diodes to check voltage drop
PMOS
Source
This circuit switches from battery to USB-C power supply if USB-C cable is connected
Board PWR LED
LDO->1.8V
This line is USB-C power line (VBUS, 5 V and 0.5 A)
Gate
This line is either the 2S bat (8.4V->6V) bracelet battery Or the line provided by Johann's powerboard (5V 1A)
Schotky Diode
This solderjumper is just in case my circuit doesn't work, we can cut this trace and disable USB charging to save the rest

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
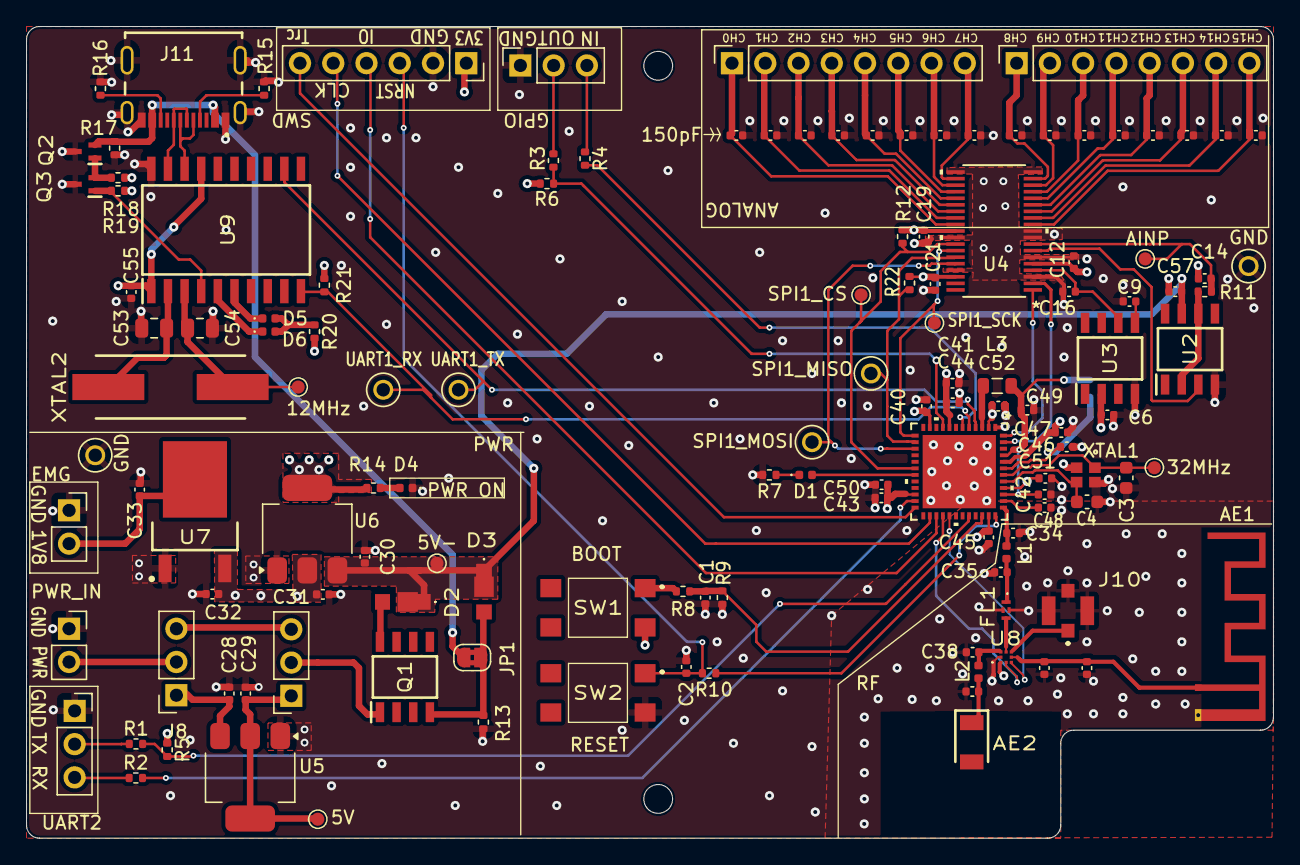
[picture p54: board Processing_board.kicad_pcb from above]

Board: 4 copper layers, 95.2 x 62.0 mm, 134 parts (1 on the bottom side), 84 nets.

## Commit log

2025-04-01 first version of circuit schematic of signal processing board
    [ADC.kicad_sch, ADC_buffer.kicad_sch, BGA8C80P3X3_290X230X100.PcbLib, EFR32BG13P732F512GM48-D.SchLib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]
2025-04-02 the 2nd (hopefully final) version of circuit diagram
    [ADC.kicad_sch, Processing_board.kicad_sch, STM32_power_supply_scheme.kicad_sch, usb_c.kicad_sch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]
2025-04-09 added reset button
    [ADC.kicad_sch, Processing_board.kicad_pcb, Processing_board.kicad_sch, STM32_power_supply_scheme.kicad_sch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]
2025-04-10 addressed all reviews except the LDO 5V
    [ADC.kicad_sch, Processing_board.kicad_sch, usb_c.kicad_sch, voltage_adaptation.kicad_sch]
2025-04-10 5V LDO and jumper cables to handle 2S battery OR johann's powerline
    [Processing_board.kicad_sch, voltage_adaptation.kicad_sch]
2025-04-16 3 RF antennas
    [ADC.kicad_sch, Processing_board.kicad_sch, RF.kicad_sch, STM32WB55_DB_QFN48_P.PcbDoc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]
2025-04-18 added all footprints, ready (?) to design PCB
    [ADC.kicad_sch, ECS-120-18-5PX-CKM-TR.stp, LD1117D33TR.stp, Processing_board.kicad_pcb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]
2025-04-23 first draft of PCB almost done
    [ADC.kicad_sch, ADS7953SBDBT.stp, AMCA31-2R450G-S1F-T3.stp, BGS13SN8E6327XTSA1.stp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]
2025-04-24 more progress
    [Processing_board.kicad_pcb, Processing_board.kicad_sch]
2025-04-25 ELEA V1
    [CX2016DB32000D0FLJCC.STEP, Processing_board.kicad_pcb, RF.kicad_sch]
2025-04-25 small changes
    [Processing_board.kicad_pcb]
2025-04-28 changed antenna placement and added GND pour on layer1 and 4
    [Processing_board.kicad_pcb, RF.kicad_sch]
2025-04-28 minor changes to correct DRC warnings
    [RF.kicad_sch]
2025-04-28 more minor cleanup
    [ADC.kicad_sch, DMN66D0LT-7.stp, PN5260.STEP, Processing_board.kicad_pcb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]
2025-04-28 added 3D models of testing pads
    [Processing_board.kicad_pcb]
2025-04-29 more cleanup
    [ADC.kicad_sch, Block_Diagram.kicad_sch, Processing_board.kicad_pcb, Processing_board.kicad_sch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]
2025-04-30 had to rename all components on the PCB to match the schematic
    [ADC.kicad_sch, Processing_board.kicad_pcb, Processing_board.kicad_sch, RF.kicad_sch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]
2025-05-01 created BOM, deleted useless folder Components and renamed CAD_Models to Parts
    [ADC.kicad_sch, ADS7953SBDBT.stp, AMCA31-2R450G-S1F-T3.stp, BGA8C80P3X3_290X230X100.PcbLib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]
2025-05-01 changed folder name back to CAD models because of compatibility
    [ADS7953SBDBT.stp, AMCA31-2R450G-S1F-T3.stp, BGS13SN8E6327XTSA1.stp, CONMHF1-SMD-G-T.stp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]
2025-05-02 correct text height/width for silkscreen, correct 3D models for THT pin headers
    [ADC.kicad_sch, Pin Header 1x2 TH Pitch 2.54mm.stp, Pin Header 1x3 TH Pitch 2.54mm.stp, Pin Header 1x6 TH Pitch 2.54mm.stp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]
2025-05-02 added N-Pulse logo etc, added open jumper solder bridge between pins VDD11 and VDDRFPA just in case
    [Processing_board.kicad_pcb, STM32_power_supply_scheme.kicad_sch]
2025-05-02 add 100nF to OPA192 power pin
    [ADC.kicad_sch, Processing_board.kicad_pcb]
2025-05-05 last changes before ordering
    [Processing_board.kicad_pcb, Processing_board.kicad_sch, usb_c.kicad_sch]
2025-05-06 correct the position of silkscreen indications
    [Processing_board-B_Cu.gbr, Processing_board-B_Mask.gbr, Processing_board-B_Paste.gbr, Processing_board-B_Silkscreen.gbr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]
2025-05-06 last commit before manufacturing inch'allah
    [Processing_board.kicad_pcb]
2025-05-22 added Block Diagram (in KiCad and PDF) ; minor silkscreen cleanup
    [$BOM.csv, ADC.kicad_sch, Block_Diagram.kicad_sch, Processing_board-B_Cu.gbl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]
2025-05-29 UART3 doesn't exist, modified block diagram
    [Block_Diagram.kicad_sch, Processing_board.kicad_sch]
2025-08-31 Added Project Report and powerpoint
2025-09-06 connected VDDRF to 3V3, but errors still remaining
    [Processing_board.kicad_pcb, Processing_board.kicad_sch, STM32_power_supply_scheme.kicad_sch]
2025-09-06 rewired buttons BOOT and RESET correctly to avoid short circuit
    [Processing_board.kicad_pcb, Processing_board.kicad_sch]
2025-09-08 changed UART3 to GPIO and rewired accordingly
    [Processing_board.kicad_pcb]
2025-09-08 created file to track changes made to the PCB
